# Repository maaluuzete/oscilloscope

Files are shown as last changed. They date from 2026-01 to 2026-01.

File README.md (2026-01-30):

# Oscilloscope

A small portable oscilloscope, made with curiosity! I'm a **technical high school student in Electrotechnics**, and during one full semester we studied oscilloscopes: how they work, how signals are displayed, how to read time and voltage scales, trigger behavior, measurements, and practical use in electronics labs.  
At some point, a thought naturally came up: now that I understand how an oscilloscope works… why not build one myself
So I did hihi!
This project is a compact digital oscilloscope, including schematic, PCB, firmware, and even the case design.  
It features a color TFT display with a classic oscilloscope grid, adjustable vertical and horizontal scales, configurable trigger (rising or falling edge), and automatic measurements such as Vpp, Vrms, and signal frequency.  
The interface is controlled using rotary encoders, and the device boots with a custom splash screen, because instruments can be functional and cute. The overall aesthetic was intentionally designed to be soft and friendly, with pastel tones and a personal touch that makes it feel less like a lab instrument and more like something made by a person who genuinely enjoys electronics.

## Screenshots
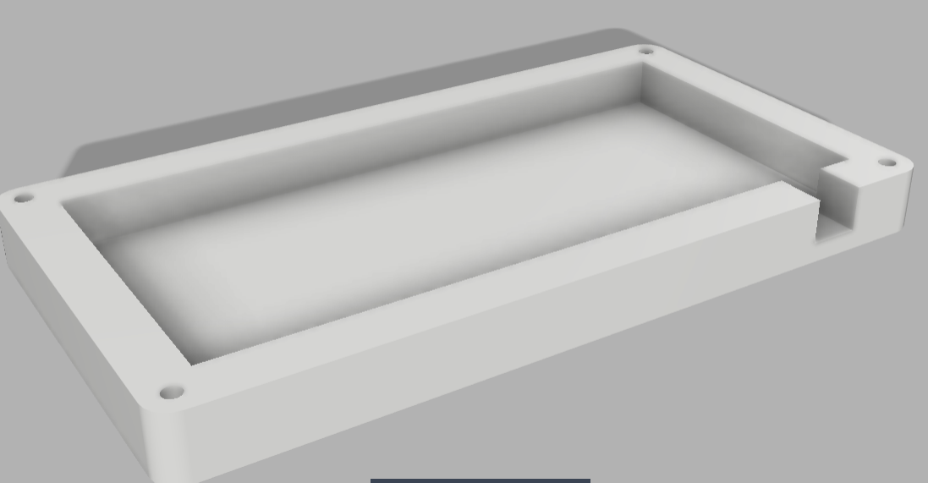
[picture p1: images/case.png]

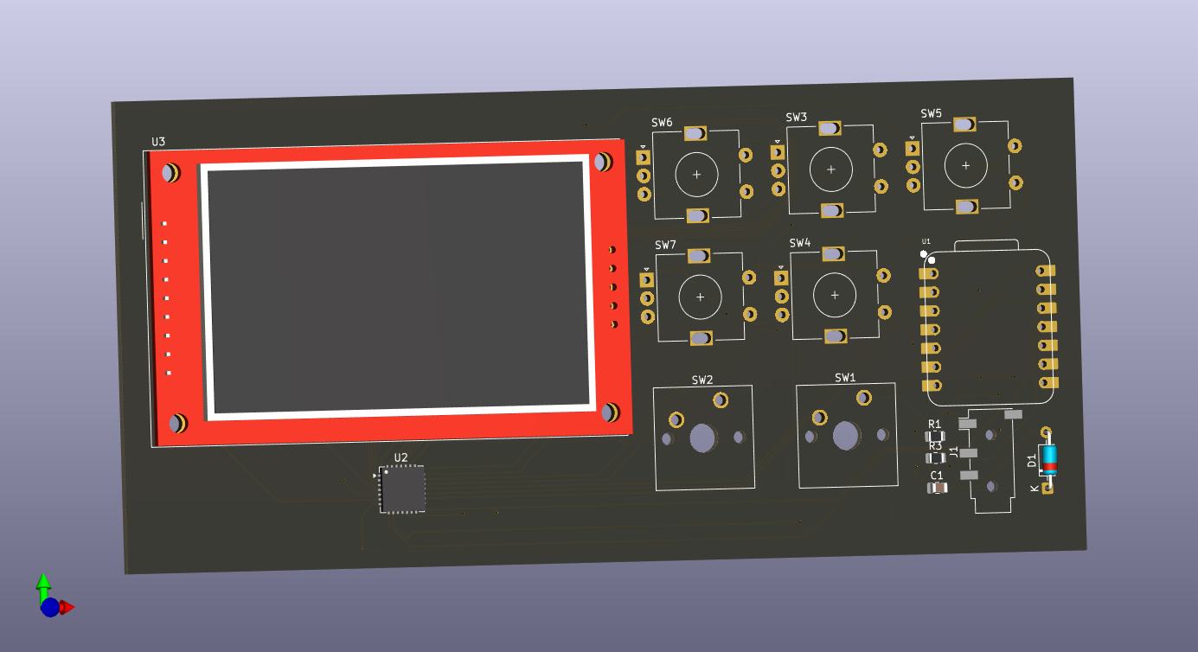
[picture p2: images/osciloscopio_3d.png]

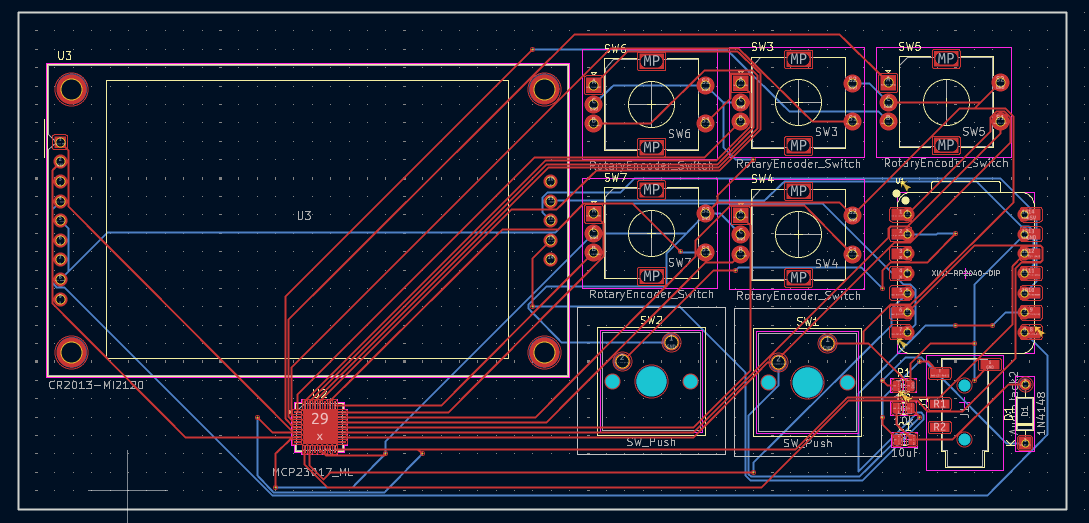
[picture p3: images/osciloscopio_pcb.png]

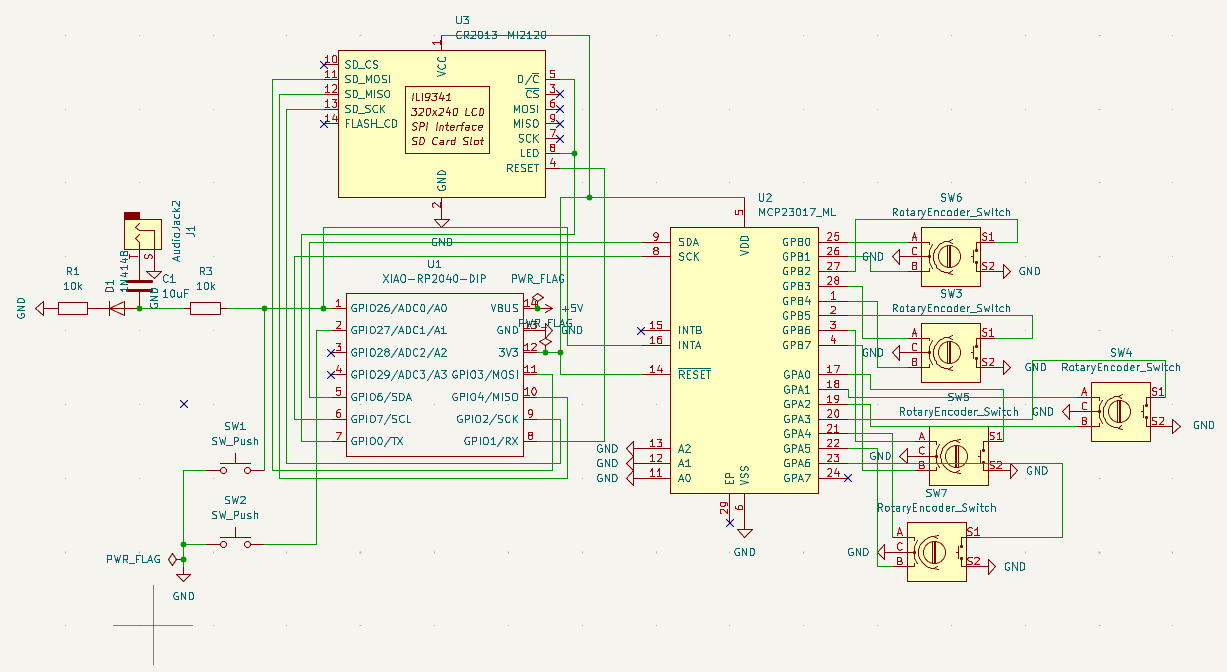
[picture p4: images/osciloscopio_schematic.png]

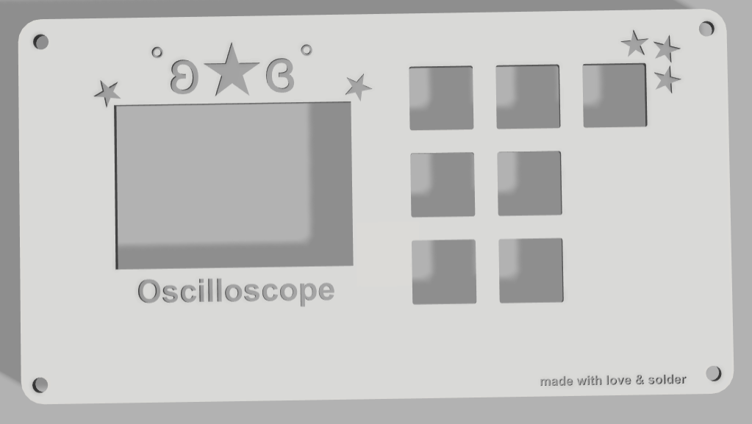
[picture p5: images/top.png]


## Project Structure
```
/
├── case/
│ ├── toposciloscopio.step
│ ├── toposciloscopio.stl
│ ├── osciloscopiocase.step
│ └── osciloscopiocase.stl
│
├── firmware/
│ ├── osciloscopio_firmware.ino
│ └── test.py
│
├── images/
│ ├── case.png
│ ├── oscilloscopio_3d.png
│ ├── oscilloscopio_pcb.png
│ ├── oscilloscopio_schematic.png
│ └── top.png
│
├── pcb/
│ ├── gerbers/
│ ├── osciloscopio.csv
│ ├── osciloscopio.kicad_pcb
│ ├── osciloscopio.kicad_pro
│ └── osciloscopio.kicad_sch
├── LICENSE
└── README.md
```

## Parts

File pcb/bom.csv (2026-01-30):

Reference | Quantity | Part Description | Link | Approx. Price (D)
PCB | 1 | base for oscilloscope | https://cart.jlcpcb.com/ | 19.67
Case and Top | 1 | 3d | ... | ~10
U1 | 1 | Seeed Studio XIAO RP2040 Microcontroller | https://www.eletrogate.com/placa-de-desenvolvimento-rp2040?gad_source=1&gad_campaignid=22470016551&gbraid=0AAAAADqxjs-fSvxIv98YjMzLoYDhcv_B6 | 6.55
U2 | 1 | MCP23017 I2C I/O Expander | https://shopee.com.br/product/954228207/28431720905?gad_source=1&gad_campaignid=23316803936&gbraid=0AAAAACoEtRmXZOr7VuSPU8LRcroQfILbx | 3
U3 | 1 | ILI9341 240x320 SPI TFT Display Module | https://shopee.com.br/product/1267903462/22093079922?gad_source=1&gad_campaignid=20824904870&gbraid=0AAAAACoEtRmBfffdQXMkRGNcOZwpfgX00 | 12.51
SW_Encoder | 5 | Rotary Encoder with Push Switch | https://shopee.com.br/product/343657323/17863242392?gad_source=1&gad_campaignid=21445281076&gbraid=0AAAAACoEtRnam04ftPS6gX578seTlQyAQ | 15
Jack | 1 | 3.5mm Audio Input Jack (PCB mount) | https://shopee.com.br/product/490475306/22099152563?gad_source=1&gad_campaignid=20824904870&gbraid=0AAAAACoEtRmBfffdQXMkRGNcOZwpfgX00 | 2
Total | - | - | - | 68.53

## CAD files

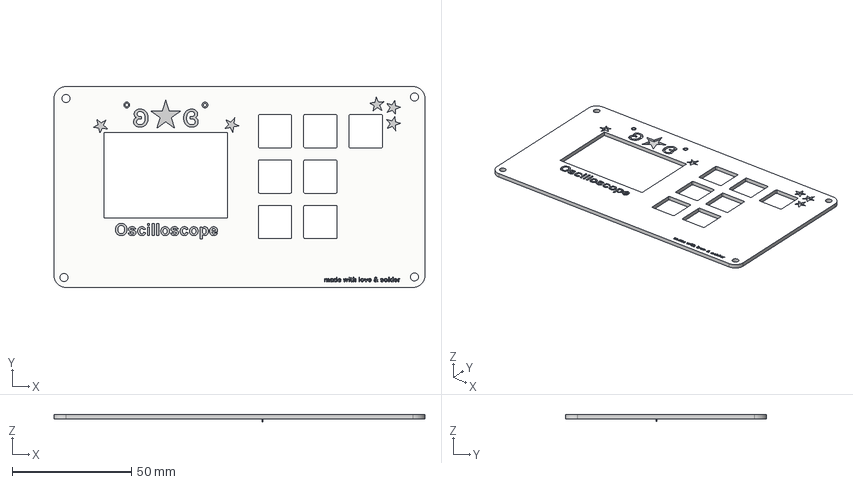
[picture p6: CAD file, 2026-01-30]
case/toposciloscopio.step
155.7 x 84.3 x 3.14 mm

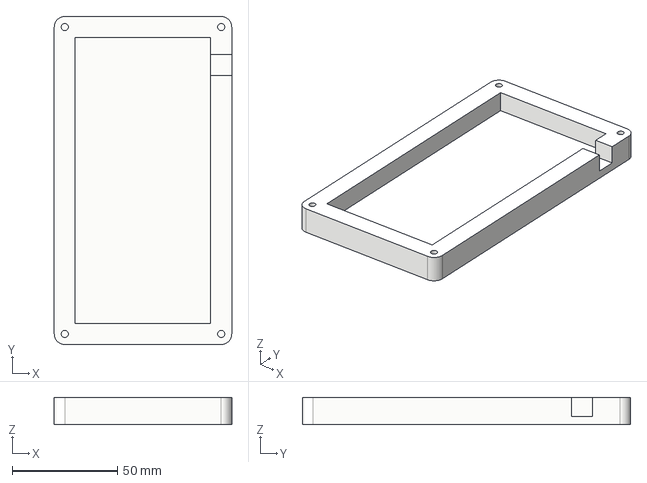
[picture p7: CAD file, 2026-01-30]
case/osciloscopiocase.step
84.3 x 155.7 x 13.0 mm

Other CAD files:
case/osciloscopiocase.stl
case/toposciloscopio.stl

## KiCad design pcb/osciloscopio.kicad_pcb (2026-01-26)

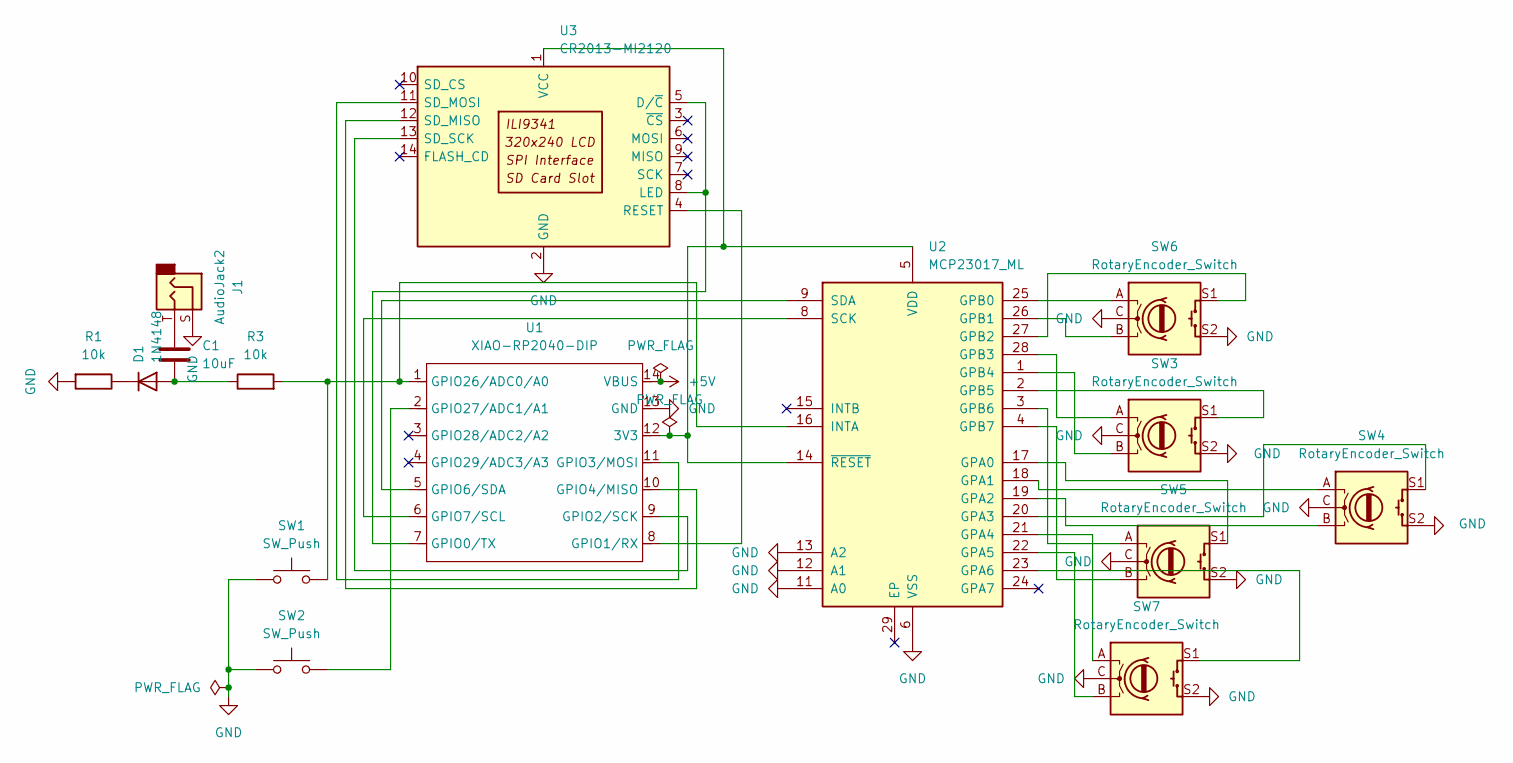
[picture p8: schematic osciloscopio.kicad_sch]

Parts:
C1: 10uF; C_0805_2012Metric
D1: 1N4148; D_DO-35_SOD27_P7.62mm_Horizontal
J1: AudioJack2; Jack_3.5mm_PJ320D_Horizontal
R1, R3: 10k; R_0805_2012Metric
SW1, SW2: SW_Push; SW_Cherry_MX_1.00u_PCB
SW3, SW4, SW5, SW6, SW7: RotaryEncoder_Switch; RotaryEncoder_Alps_EC11E-Switch_Vertical_H20mm
U1: XIAO-RP2040-DIP
U2: MCP23017_ML; QFN-28-1EP_6x6mm_P0.65mm_EP4.25x4.25mm
U3: CR2013-MI2120

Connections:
+5V: U1.14 (VBUS)
GND: J1.S, R1.2, SW1.1, SW2.1, SW3.C, SW3.S2, SW4.C, SW4.S2, SW5.C, SW5.S2, SW6.C, SW6.S2, SW7.C, SW7.S2, U1.13 (GND), U2.6 (VSS), U2.11 (A0), U2.12 (A1), U2.13 (A2), U3.2 (GND)
unnamed: C1.1, J1.T
unnamed: C1.2, D1.2 (A), R3.1
unnamed: D1.1 (K), R1.1
unnamed: U1.12 (3V3), U2.5 (VDD), U2.14 (~RESET), U3.1 (VCC)
unnamed: U1.7 (GPIO0/TX), U3.5 (D/~C), U3.8 (LED)
unnamed: U1.8 (GPIO1/RX), U3.4 (RESET)
unnamed: U1.9 (GPIO2/SCK), U3.13 (SD_SCK)
unnamed: U1.11 (GPIO3/MOSI), U3.11 (SD_MOSI)
unnamed: U1.10 (GPIO4/MISO), U3.12 (SD_MISO)
unnamed: U1.5 (GPIO6/SDA), U2.9 (SDA)
unnamed: U1.6 (GPIO7/SCL), U2.8 (SCK)
unnamed: R3.2, SW1.2, U1.1 (GPIO26/ADC0/A0), U2.16 (INTA)
unnamed: SW2.2, U1.2 (GPIO27/ADC1/A1)
unnamed: SW5.S1, U2.17 (GPA0)
unnamed: SW4.A, U2.18 (GPA1)
unnamed: SW4.B, U2.19 (GPA2)
unnamed: SW4.S1, U2.20 (GPA3)
unnamed: SW7.A, U2.21 (GPA4)
unnamed: SW7.B, U2.22 (GPA5)
unnamed: SW7.S1, U2.23 (GPA6)
unnamed: SW6.A, U2.25 (GPB0)
unnamed: SW6.B, U2.26 (GPB1)
unnamed: SW6.S1, U2.27 (GPB2)
unnamed: SW3.A, U2.28 (GPB3)
unnamed: SW3.B, U2.1 (GPB4)
unnamed: SW3.S1, U2.2 (GPB5)
unnamed: SW5.A, U2.3 (GPB6)
unnamed: SW5.B, U2.4 (GPB7)

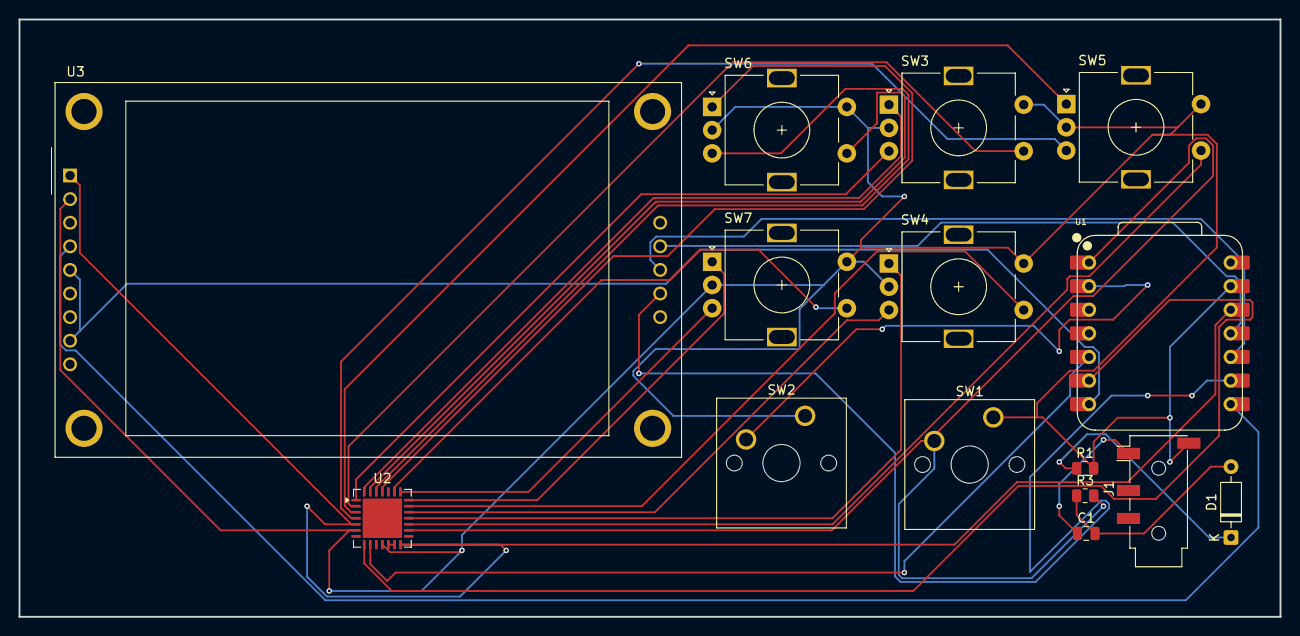
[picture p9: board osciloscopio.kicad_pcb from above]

Board: 2 copper layers, 135.7 x 64.3 mm, 15 parts (0 on the bottom side), 29 nets.

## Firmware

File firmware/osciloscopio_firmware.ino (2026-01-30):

#include <SPI.h>
#include <Adafruit_GFX.h>
#include <Adafruit_ILI9341.h>
#include <Adafruit_MCP23017.h>
#include <hardware/adc.h>
#include <math.h>

#define tft_cs 5
#define tft_dc 6
#define tft_rst 7

Adafruit_ILI9341 tft(tft_cs,tft_dc,tft_rst);
Adafruit_MCP23017 mcp;

#define signal_pin 26

int screen_w=320;
int screen_h=240;
int grid_top=20;
int grid_h=200;
int samples=320;

uint16_t raw[320];
float volts[320];

float volts_divs[]={0.1,0.2,0.5,1.0};
int volts_idx=3;

int time_divs[]={10,20,50,100,200,500};
int time_idx=3;

float vert_offset=0.0;
int horiz_offset=0;

float trigger_lvl=1.65;
bool trigger_rise=true;
bool running=true;

float meas_vpp=0.0;
float meas_vrms=0.0;
float meas_freq=0.0;

uint16_t pastel_pink=0xf3bf;
uint16_t grid_pink=0xf1ae;
uint16_t trace_cyan=0x07ff;

void splash()
{
 tft.fillScreen(pastel_pink);
 tft.setTextColor(0xffff);
 tft.setTextSize(2);
 tft.setCursor(40,90);
 tft.print("made with love");
 tft.setCursor(60,120);
 tft.print("& solder by");
 tft.setTextSize(3);
 tft.setCursor(60,155);
 tft.print("maluzete");
 delay(2500);
}

void draw_grid()
{
 tft.fillRect(0,grid_top,screen_w,grid_h,0x0000);
 for(int i=0;i<=10;i++)
 {
  int x=i*(screen_w/10);
  tft.drawFastVLine(x,grid_top,grid_h,grid_pink);
 }
 for(int i=0;i<=8;i++)
 {
  int y=grid_top+i*(grid_h/8);
  tft.drawFastHLine(0,y,screen_w,grid_pink);
 }
}

void acquire()
{
 int delay_us=(time_divs[time_idx]*10)/samples;
 for(int i=0;i<samples;i++)
 {
  raw[i]=analogRead(signal_pin);
  delayMicroseconds(delay_us);
 }
 for(int i=0;i<samples;i++)
 {
  volts[i]=(raw[i]/4095.0)*3.3;
 }
}

int find_trigger()
{
 for(int i=1;i<samples;i++)
 {
  if(trigger_rise)
  {
   if(volts[i-1]<trigger_lvl && volts[i]>=trigger_lvl){return i;}
  }
  else
  {
   if(volts[i-1]>trigger_lvl && volts[i]<=trigger_lvl){return i;}
  }
 }
 return 0;
}

void compute_measures()
{
 float vmin=10.0;
 float vmax=0.0;
 float sumsq=0.0;
 int crossings=0;
 float last_cross=0.0;
 float period_sum=0.0;

 for(int i=0;i<samples;i++)
 {
  if(volts[i]<vmin){vmin=volts[i];}
  if(volts[i]>vmax){vmax=volts[i];}
  sumsq+=volts[i]*volts[i];
 }

 for(int i=1;i<samples;i++)
 {
  if(volts[i-1]<trigger_lvl && volts[i]>=trigger_lvl)
  {
   float t=i*(time_divs[time_idx]*10e-6/samples);
   if(crossings>0){period_sum+=t-last_cross;}
   last_cross=t;
   crossings++;
  }
 }

 meas_vpp=vmax-vmin;
 meas_vrms=sqrt(sumsq/samples);
 if(crossings>1){meas_freq=1.0/(period_sum/(crossings-1));}
 else{meas_freq=0.0;}
}

void draw_wave()
{
 int trig=find_trigger();
 for(int i=1;i<screen_w;i++)
 {
  int i1=trig+i-1+horiz_offset;
  int i2=trig+i+horiz_offset;
  if(i2>=samples){break;}
  float v1=volts[i1]-vert_offset;
  float v2=volts[i2]-vert_offset;
  int y1=grid_top+grid_h/2-(v1/volts_divs[volts_idx])*(grid_h/8);
  int y2=grid_top+grid_h/2-(v2/volts_divs[volts_idx])*(grid_h/8);
  tft.drawLine(i-1,y1,i,y2,trace_cyan);
 }
}

void draw_ui()
{
 tft.fillRect(0,0,screen_w,20,0x0000);
 tft.setTextColor(0xffff);
 tft.setTextSize(1);
 tft.setCursor(5,5);
 tft.print(volts_divs[volts_idx]);
 tft.print("v/div ");
 tft.print(time_divs[time_idx]);
 tft.print("us/div");
 tft.setCursor(170,5);
 tft.print("vpp:");
 tft.print(meas_vpp,2);
 tft.setCursor(240,5);
 tft.print("hz:");
 tft.print(meas_freq,1);
}

void setup()
{
 adc_init();
 adc_gpio_init(signal_pin);
 tft.begin();
 tft.setRotation(1);
 mcp.begin();
 for(int i=0;i<16;i++)
 {
  mcp.pinMode(i,INPUT);
  mcp.pullUp(i,HIGH);
 }
 splash();
 draw_grid();
}

void loop()
{
 if(running)
 {
  acquire();
  compute_measures();
  draw_grid();
  draw_wave();
  draw_ui();
 }
 if(!mcp.digitalRead(14))
 {
  running=!running;
  delay(300);
 }
}

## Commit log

2026-01-26 Refactor code structure for improved readability and maintainability
    [osciloscopio-B_Cu.gbr, osciloscopio-B_Mask.gbr, osciloscopio-B_Paste.gbr, osciloscopio-B_Silkscreen.gbr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]
2026-01-26 Revise component details in osciloscopio.csv
    Updated component list in osciloscopio.csv.
    [osciloscopio.csv]
2026-01-30 Its finished! The firmware and the readme.md
    [osciloscopiocase.step, osciloscopiocase.stl, toposciloscopio.step, toposciloscopio.stl]
2026-01-30 bom.csv finished
    [bom.csv, osciloscopio.csv]
